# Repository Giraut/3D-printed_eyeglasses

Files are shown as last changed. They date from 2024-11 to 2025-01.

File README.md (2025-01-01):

# 3D-printed eyeglasses
### Version 1.4

Those are the CAD files for the frames of the spectacles I wear every day. When I break the frames, or if I want a new color for a bit of diversity, I simply print new frames and reuse the lenses.

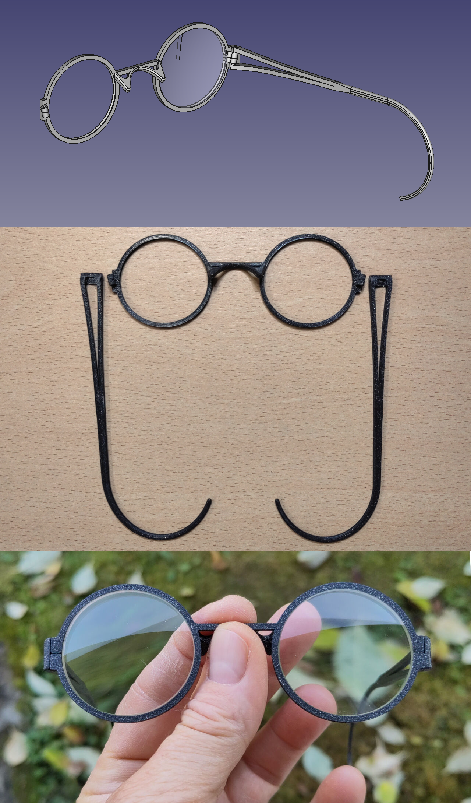
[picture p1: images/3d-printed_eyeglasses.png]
3D-printed eyeglasses

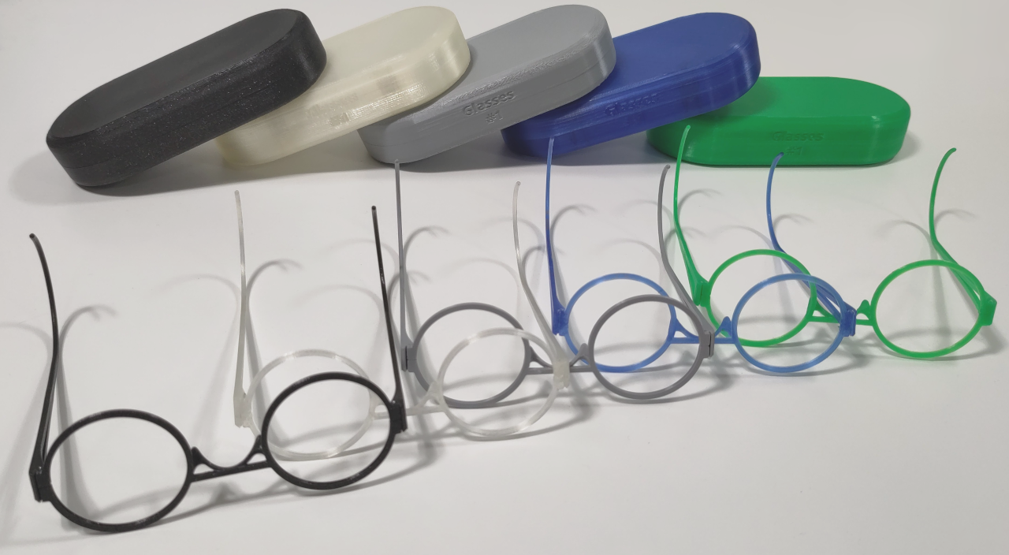
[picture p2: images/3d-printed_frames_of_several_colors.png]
3D-printed frames of several colors

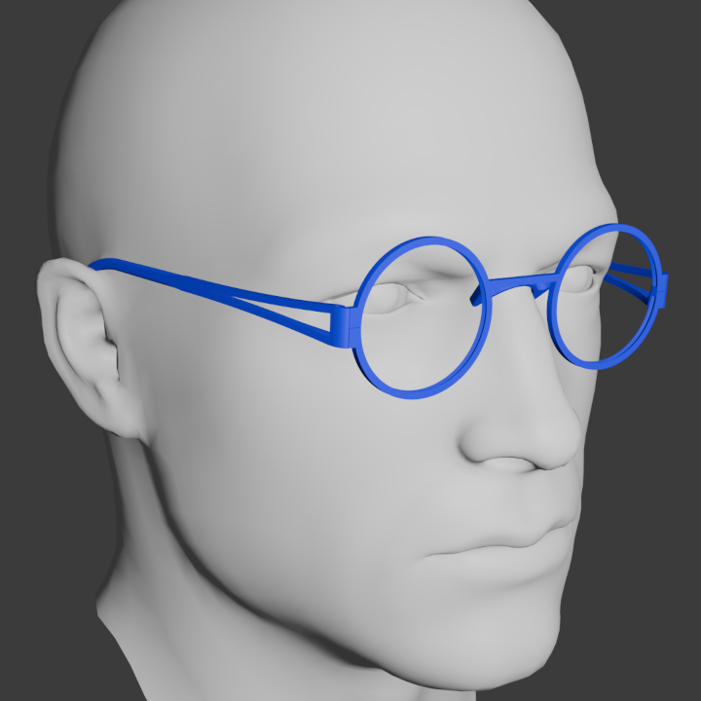
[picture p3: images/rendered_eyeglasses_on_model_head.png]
Rendered eyeglasses on model head


* [Files](#files)
* [Explanation of the registration tabs](#explanation-of-the-registration-tabs)
* [Printing](#printing)
* [Ordering lenses](#ordering-lenses)
* [Assembly](#assembly)
* [Customizing](#customizing)
* [Custom case](#custom-case)
* [Clip-on shades for round 38.8mm-diameter lenses](#clip-on-shades-for-round-388mm-diameter-lenses)
* [Clip-on shades with novelty mesh lenses](#clip-on-shades-with-novelty-mesh-lenses)
* [Custom case for the clip-on shades](#custom-case-for-the-clip-on-shades)

## Files

### Frames proper

Final frames in which the lenses are mounted. The lens holders feature lens registration tabs in the V-grooves at the split hinges (see below).

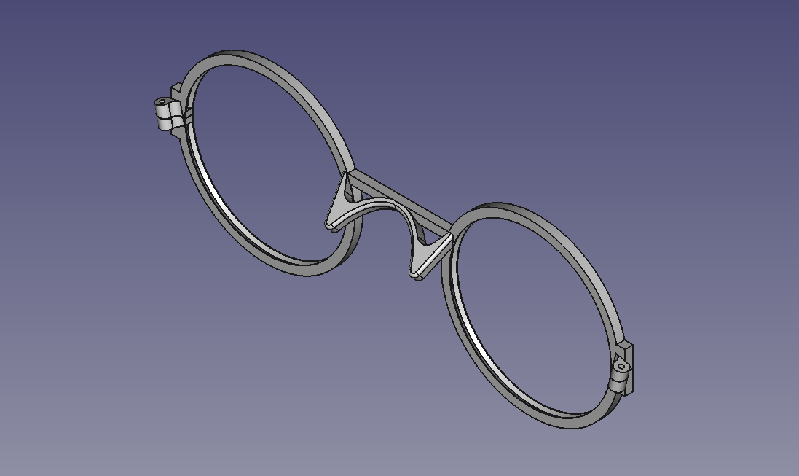
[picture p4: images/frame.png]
Frame


- [FreeCAD model for the frame](frame.FCStd)
- [3MF model for the frame](frame.3mf)

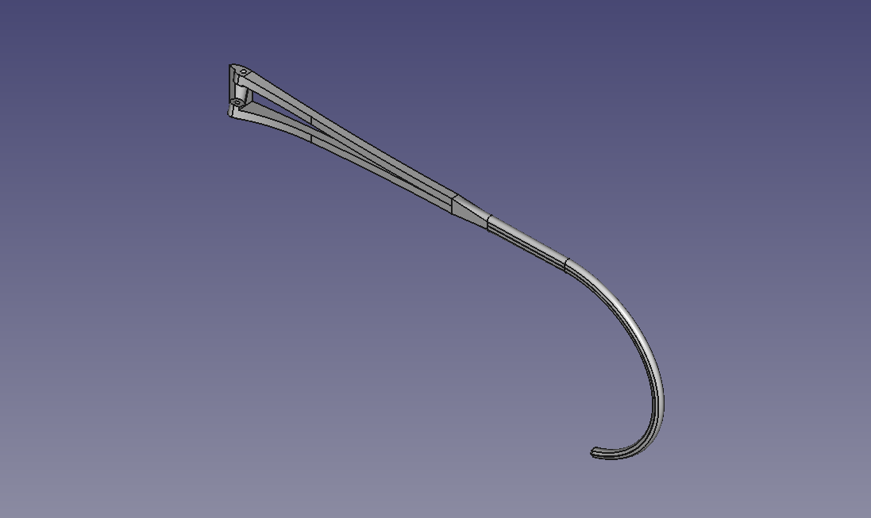
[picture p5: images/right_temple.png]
Right temple


- [FreeCAD model for the right temple](right_temple.FCStd) (the left temple is the mirror)
- [3MF model for the right temple](right_temple.3mf) (the left temple is the mirror)

### Template for the lens manufacturer

This template is supplied to the lens manufacturer: the lens holders have the same geometry as the final frames but the template is square and stiffer to facilitate mounting in the [lens edging machine](https://youtu.be/dKXUWH8gQLU), the V-groove is slightly deeper than the V-groove in the final frames and the registration tabs are absent to avoid snagging on the edging machine's tracer.

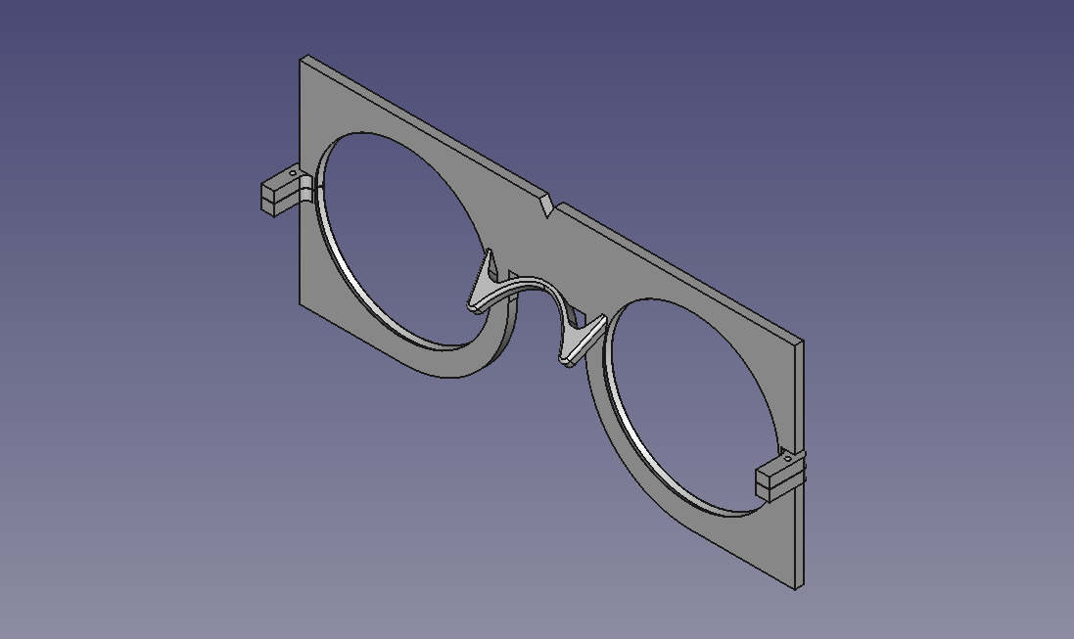
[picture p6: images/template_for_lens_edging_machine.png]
Template for lens edging machine


- [FreeCAD model for the edging machine template](template_for_lens_edging_machine.FCStd)
- [3MF model for the edding machine template](template_for_lens_edging_machine.3mf)

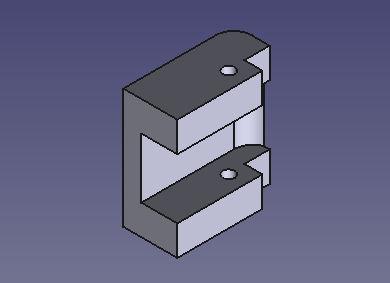
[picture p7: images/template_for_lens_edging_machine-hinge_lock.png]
Template for lens edging machine - Hinge lock


- [FreeCAD model for the edging machine template's fake hinges' locking piece](template_for_lens_edging_machine-hinge_lock.FCStd) (2 needed per template)
- [3MF model for the edging machine template's fake hinges' locking piece](template_for_lens_edging_machine-hinge_lock.3mf) (2 needed per template)

### Optional hinge pin jig

Optionally, this jig can be printed to hold the frames at a 13° angle so that the hinges' axes are vertical, to drive the pins in or out of the hinges with a press.

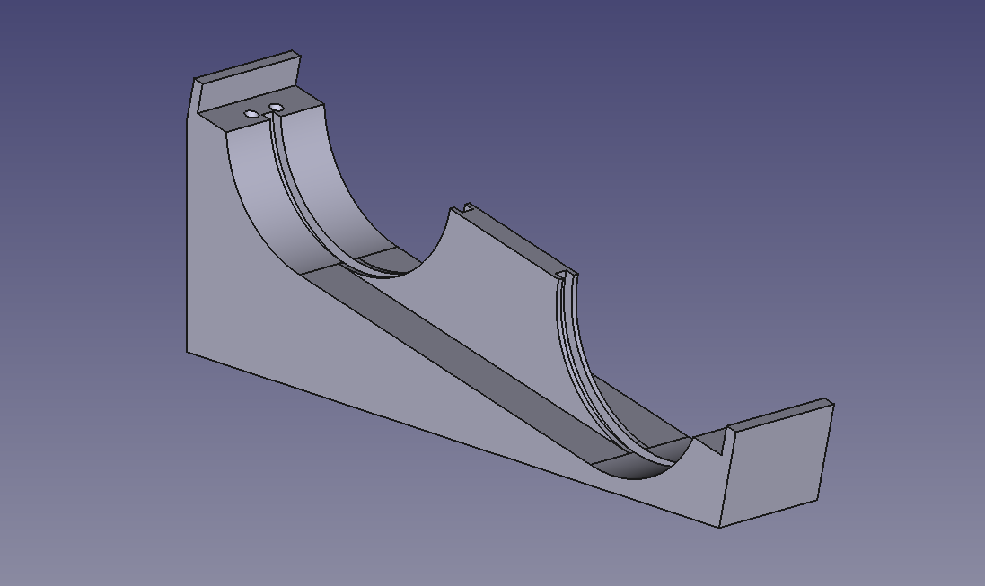
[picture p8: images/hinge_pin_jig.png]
Hinge pin jig


- [FreeCAD model for the hinge pin jig](hinge_pin_jig.FCStd)
- [3MF model for the hinge pin jig](hinge_pin_jig.3mf)

### Additional details for the lens manufacturer

A few details the lens manufacturer needs to choose the grinding wheel with the correct bevel profile ("hide-a-bevel"-type bevel, 120° angle) and the width and position of the lens registration tabs if you want them to file it for you - and they agree to do it of course:

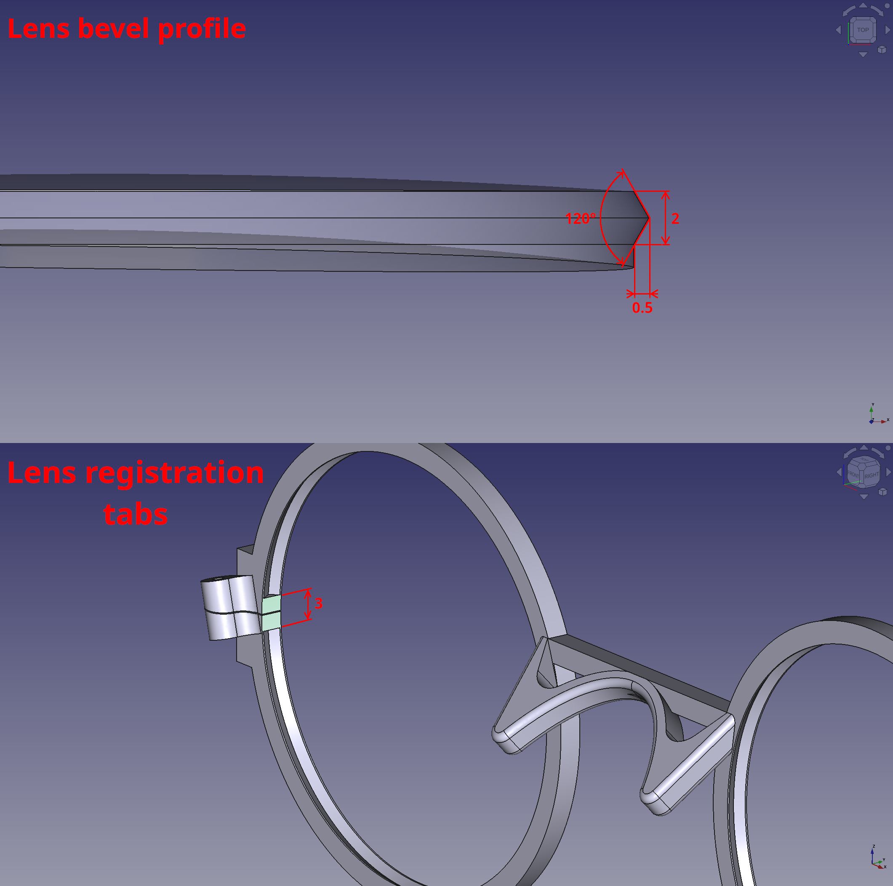
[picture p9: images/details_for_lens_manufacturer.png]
Details for the lens manufacturer


## Explanation of the registration tabs

The final frames feature lens registration tabs around the split hinges that interrupt the V-grooves. Those tabs orient the lenses correctly, which is important for astigmat lenses particularly. In this frame design, they also help lock the frame closed.

The tabs are required because the lenses are almost round. They provide a positive mechanical stop to prevent the lenses from shifting and turning in the lens holders, but they require filing a 3.5mm-wide notch in the lenses' bevel.

This type of lens registration is almost never used in round glasses because the frame itself is usually made of a material strong enough to clamp the lenses solidly in place, or the lenses are glued in place. Also, they're difficult to manufacture with traditional machining methods.

Those 3D-printed glasses provide very little clamping force, and glue isn't ideal to routinely and quickly install the lenses into new frames without damaging them. But it's trivially easy to print the registration tabs inside the V-grooves with a 3D printer.

Notching the bevel of the lenses is a one-off job, so this registration solution is more desirable if you want to change frames often. But it does require a square needle file, and more importantly, being handy with one. And it does require a small vise with rubber jaws, covering the lenses with scotch tape to avoid scratching them when they're clamped in the vise, and working up the nerves to files through your brand new, multi-hundred-dollar lenses if your prescription is very special.

If you don't think you can do it, point your lens manufacturer or your local optician to this page and ask them if they can do it for you. The lens manufacturer probably won't have time for this, but your local optician most certainly will if you order through them - but for a price of course. But again, it's a one-off job and after that, your new frames will always be free and you'll be able to mount the lenses yourself at home in a couple of minutes 🙂

## Printing

You can print the frames in any material you want, even PLA. Prefer low layer heights and print at lower speeds to get better details and more accuracy for the hinge pin holes and the V-groove profile. 0.2mm works, but 0.15mm or even 0.10mm is better. Print the lens holder front face down and the temples outer face down, so the visible surfaces when you wear the glasses look the smoothest and nicest.

## Ordering lenses

- Print the template and 2 fake hinge locking pieces.
- Split the hinges with an X-Acto knife or a razor blade.
- Close each hinge with a locking piece and secure it with a small piece of 1mm piano wire or similar.
- Send the template to the lens manufacturer or give it to your optician along with your prescription and tell them you want to receive the lenses mounted with the proper orientation in the lens holders with the 3 alignment dots marked on each lens! This is very important if you want to notch the bevels yourself. Otherwise ask the lens manufacturer or the optician to do it for you: they'll know what to do.

## Notching the lenses

- Insert the lenses in the template if they didn't come back from the lens manufacturer or the optician already mounted in it.
- Lightly squeeze the fake hinges with your fingers and line up all 6 alignment dots on the lenses.
- Close the fake hinges with the locking pieces.
- Ensure the lenses are positioned properly by placing the template on your nose like real glasses and ensuring you can see well through the lenses. Don't notch the lenses unless your vision is perfect at this point!
- With a thin sharpie, mark the location of the split hinge on each lens, front and back.
- Remove the lenses from the template and draw a line between the two marks on each lens, across the thickness of the lens, straddling the bevel.
- Cover the lenses in scotch tape to avoid damaging them in the vise.
- File a 3.5mm-wide notch into the bevel centered on the line on each lens. Don't file any deeper than the height of the bevel, otherwise the notch will be visible when the lens is mounted in the frame!

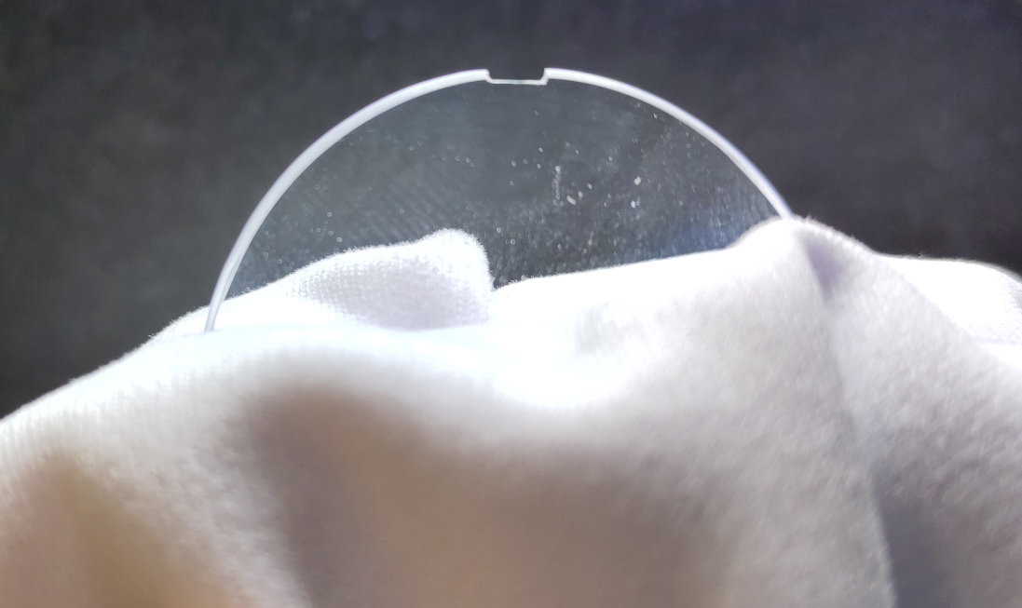
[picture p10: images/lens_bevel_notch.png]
Lens bevel notch


## Assembly

### Extra components needed

- 2 x [1x10mm dowel pins](https://www.mcmaster.com/91585A091/)

### Instructions

- After printing, crack off the supports.
- Ream the hinge pin holes on the frame and both temples with a 0.9mm drillbit, then as little as possible with a 1.0mm drillbit. Be careful when you insert the drillbits: the axes of the hinges are angled 13° vertically to allow the temples to fold up and fit in a regular glasses case. If you insert the drillbits straight vertically, you will damage the hinges!

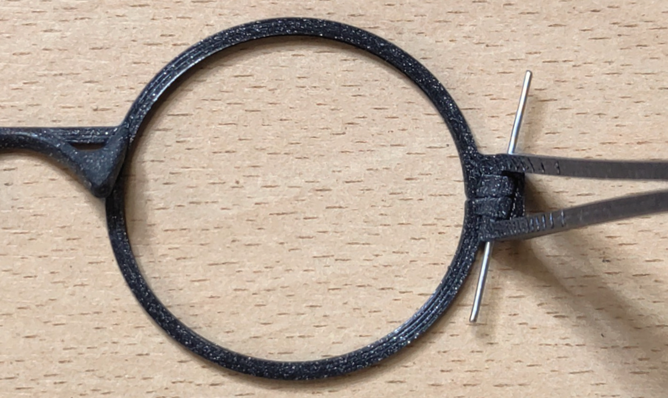
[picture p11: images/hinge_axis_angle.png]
Hinge axis angle

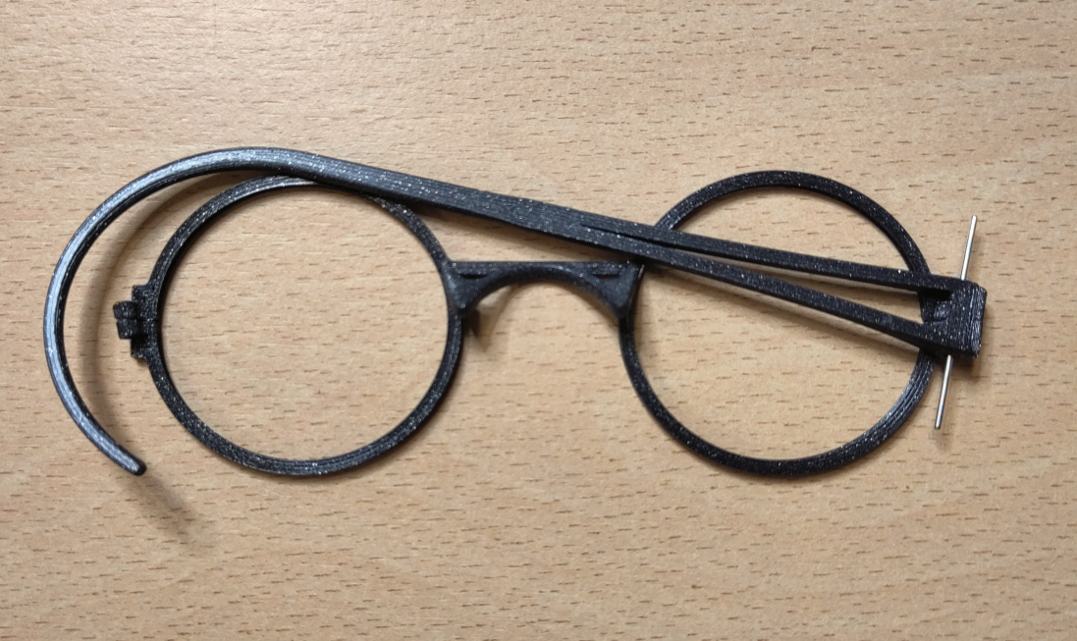
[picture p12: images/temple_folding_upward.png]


- Insert each lens into its holder with the notch facing the hinge.

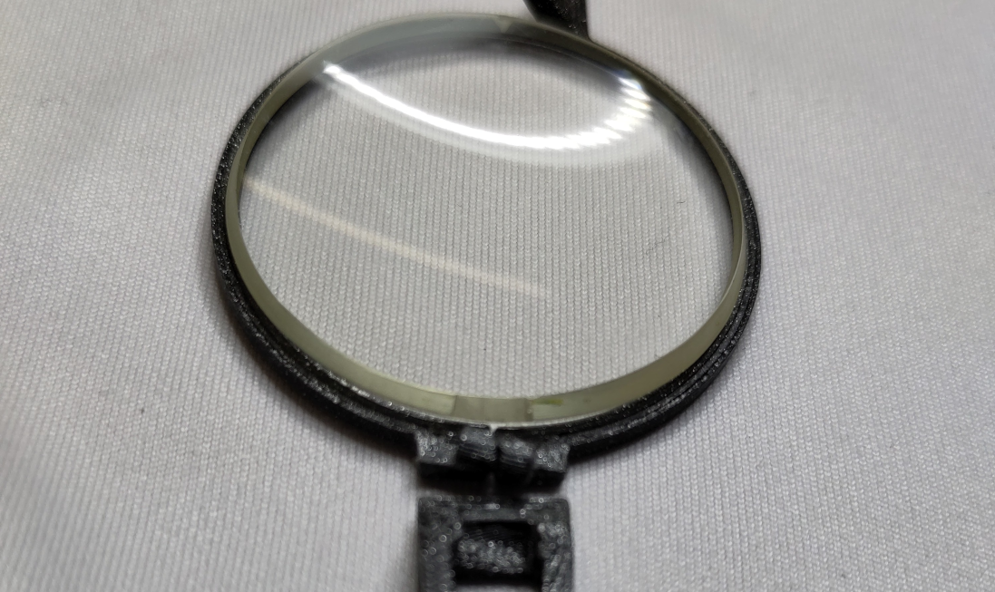
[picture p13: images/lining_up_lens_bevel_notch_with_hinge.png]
Lining up the lens bevel notch with the hinge


- Orient each lens until both halves of the hinge drop into the notch and the hinge closes completely.

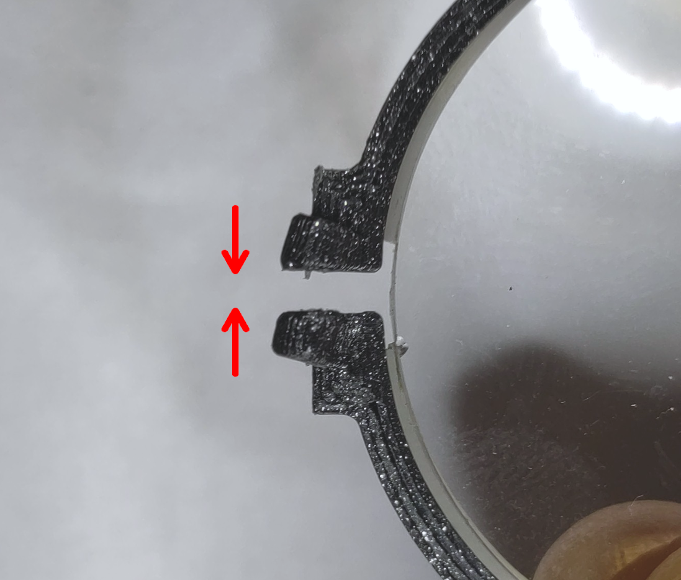
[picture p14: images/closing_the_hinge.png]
Closing the hinge


- Fit the temples onto the hinges.
- Drive a dowel pin through each temple and hinge to hold everything together.

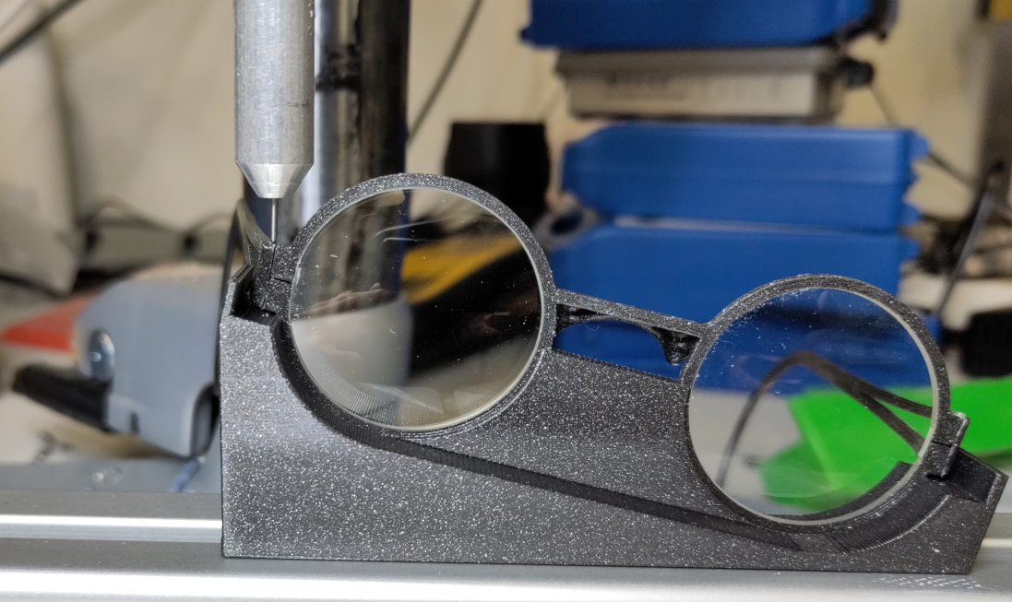
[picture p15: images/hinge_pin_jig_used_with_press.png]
Hinge pin jig used_with press


## Customizing

The parts in these FreeCAD model files are designed to create frames that fit me perfectly. But everybody's head is different.

The traditional way to adjust off-the-shelf eyeglasses is to soften and bend the frame and temples. But with 3D-printed frames, it is far better to print them exactly right for you: that way, little to no rework is required after printing new parts.

The frames should naturally drop on the roof of your nose, the temples should drop on the root of your ears and the temple wires should wrap around your ears such that:

- The glasses fit perfectly on your face with **ZERO** internal stress: PLA is quite bendy and these frames are very thin, so it doesn't take much tension to bend them out of shape and compromise the placement of the lenses. The frames should have the exact same shape on your face that they have when resting on a table.
- The glasses stay put on your nose and don't slide down.
- Each lens is perfectly centered on the corresponding eye.
- the lenses don't sit at an angle vertically - i.e. they're normal to your line of sight.

### Adjusting the temples splay

These frames are an older style design. They're copies of my nickel silver frames which I made myself some 20 years ago, themselves copies of vintage 1910 glasses I found at the flea market that I really liked. I believe this style is now called "John Lennon", but it's much older than that.

Frames in that style are much narrower than the wearer's head. The idea is to bring the lenses as close to the eyes as possible to provide a very wide field of view with small lenses and make the temples almost touch the sides of the head over their entire length (very convenient incidentally: you can sleep on your side with your glasses on without damaging them!).

For that reason, the frames are splayed to accommodate the width of your head. In other words, the temples are not parallel but opened up.

To adjust the splay, edit the `Hinge mid profile master sketch` in the temple's FreeCAD model and change the distance between the hinges and the root of your ear and the width of your head at that point:

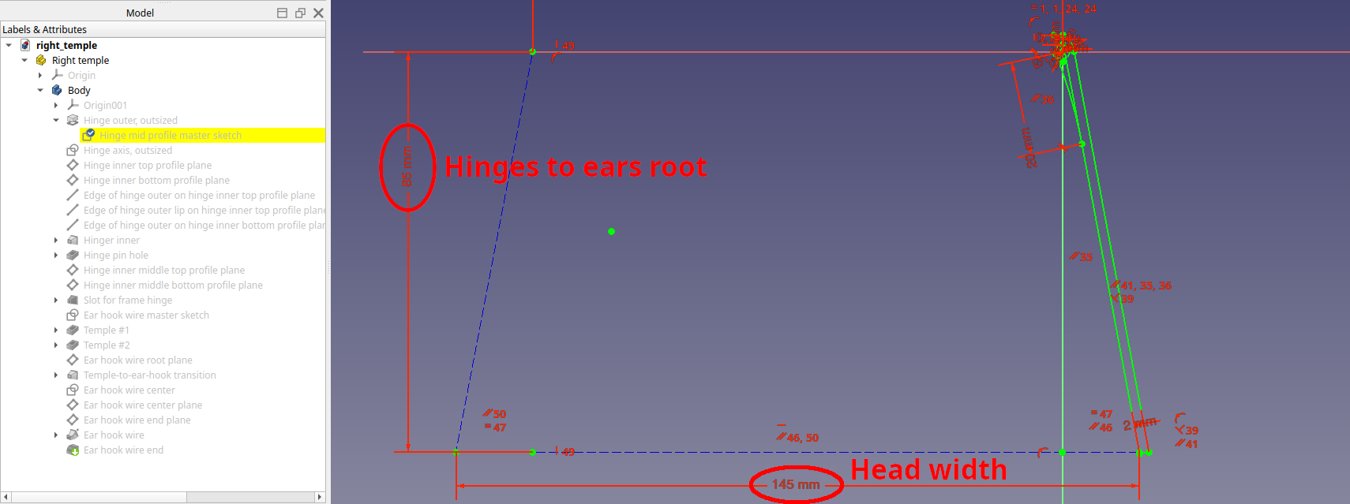
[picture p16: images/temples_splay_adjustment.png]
Temples splay adjustment


These dimensions aren't critical: they should get the splay angle in the ballpark. The temples should land on your ears without squeezing your head at all. But even if the opening is a few millimeters too narrow, the temple wires are flexible enough to bend a little without deforming the frame at the front.

Still, ideally the temples should only lightly graze the sides of your head.

## Adjusting the temple length, height and hook shape

Edit the `Ear hook wire master sketch` in the temple's FreeCAD model to change the length of the temples, modify the shape of the hooks if they don't wrap around your ears perfectly and adjust the temple drop (or rise if you reverse the dimension) to bring the lenses vertical:

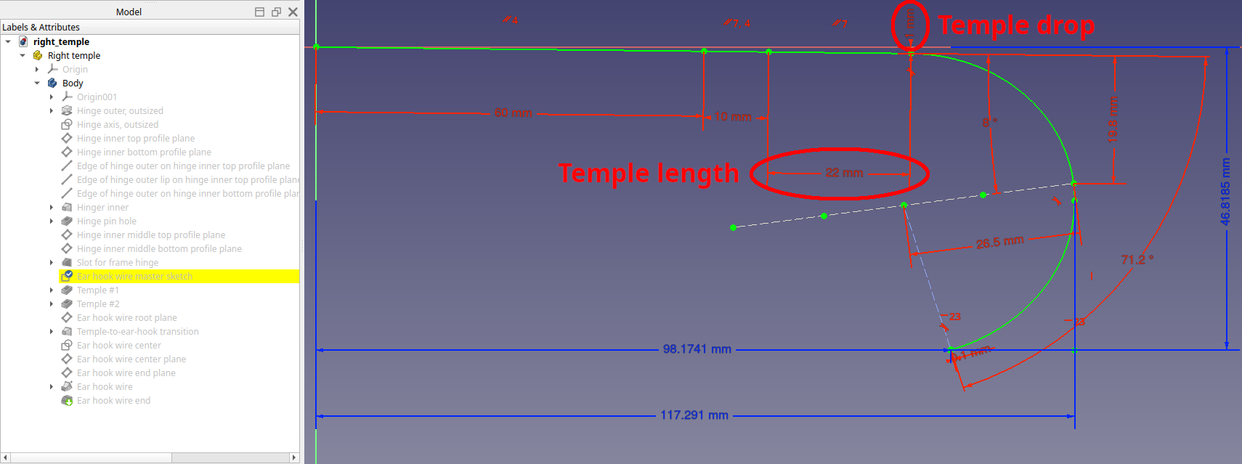
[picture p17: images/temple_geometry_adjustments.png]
Temple geometry adjustments


You may - and probably will - want adjust those parameters differently for the right and left temples if your eyes or your ears aren't level, or your ears have different shapes. Most people don't have perfectly symmetrical facial features, so it's perfectly normal.

To determine if the geometry of the left and right temple are correct:

- Don the glasses and let them sit on your nose and ears naturally.
- If a hook pulls on the back of your ear, the temple on that side is too short.
- If you pull gently on a temple and let go of it and that side of the frame stays low on your nose, the temple on that side is too long.
- If the end of a wire digs into the bottom of your ear, the wire hook on that side is too narrow.
- If the wire only rests on the top half of your ear and doesn't touch the bottom, the wire hook on that side is too wide.

Look straight ahead:

- If the frame looks like an unbroken circle and it looks like you're looking through a single hoop, the temple lengths and drops are dead-on.
- If the circle looks broken but the two halves look like they're the same diameters, you'll need to increase the drop on the side the half-circle appears lower.
- If the circle looks broken but the two halves look like they're at the same level but different diameters, you'll need to increase the length of the temple on the side the half-circle looks larger.

Those adjustments are sometimes mere millimeters and are done by trial and error - i.e. print, test for fit, re-print, re-test for fit... until the glasses fit perfectly and feel really comfortable.

It's a bit tedious but it's a one-off job: once it's done, you'll get perfectly-fitting glasses out of your printer each and every time.

## Adjusting the nose bridge

If the nose bridge is too narrow, it will feel like it's digging into the sides of your nose when wearing the glasses for a long time. If it's too wide, it will feel heavy on top of your nose over time.

You can adjust the shape of the bridge by editing the `Nose bridge profile` sketch in the frame's FreeCAD model. Unfortunately, this sketch has a lot of dependencies in other features of the model, and it's designed to merge perfectly with the decorative straight bridge at the front. So if you modify it too much, it will probably break the model. So some knowledge of modelling with FreeCAD is required to successfully alter the shape of the nose bridge so the model resolves correctly.

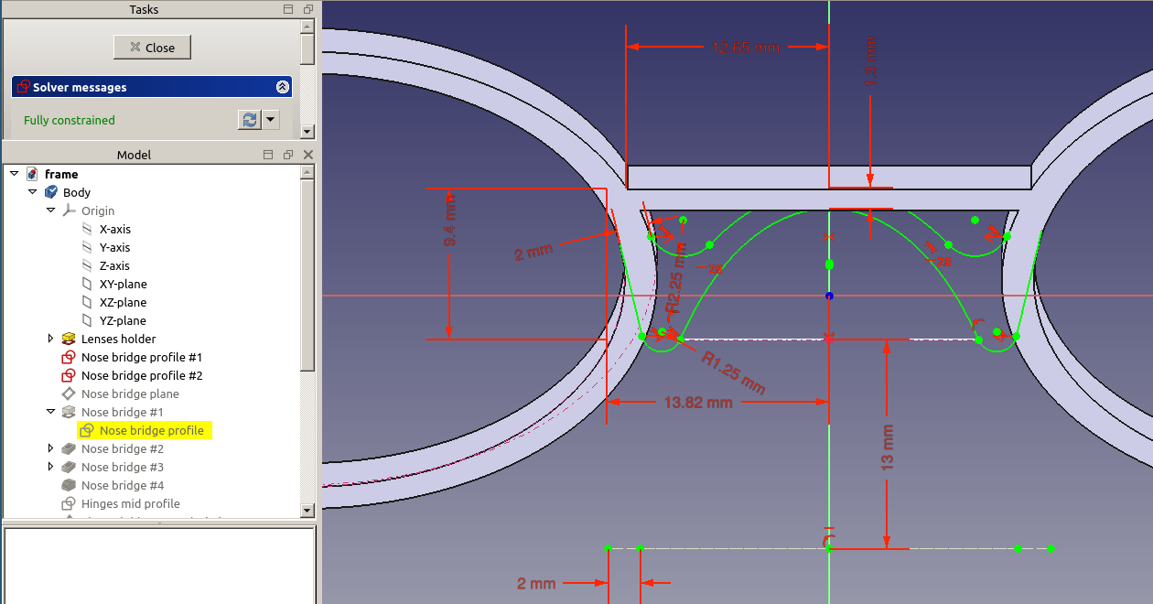
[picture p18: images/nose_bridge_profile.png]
Nose bridge profile


## Adjusting the lens holders' diameters

Depending on your particular printer and how the lens manufacturer edged the lenses exactly, the lenses may not fit perfectly inside the lens holders. You can modify the diameters of the lens holders by editing the `Lenses holder master sketch` in the frame's FreeCAD model:

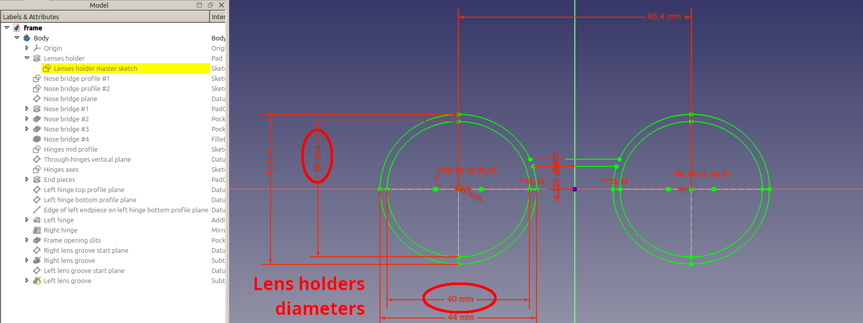
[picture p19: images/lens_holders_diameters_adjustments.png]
Lens holders diameters adjustments


The lens holders are elliptical and are nominally 40mm and 38mm in diameter. If the lenses fit loosely, reduce both diameters in steps of 0.1mm, reprint and retest for fit. If they fit too tight, increase both diameters similarly. Don't increase the diameters more tham 0.2mm to avoid compromising the frame's rigidity.

## Custom case

This case is custom-made for these glasses. It's designed to hold them by the edge of the frame only, without the lenses ever touching any part of the case, so the case doesn't need to be padded with soft material of any kind to prevent scratching:

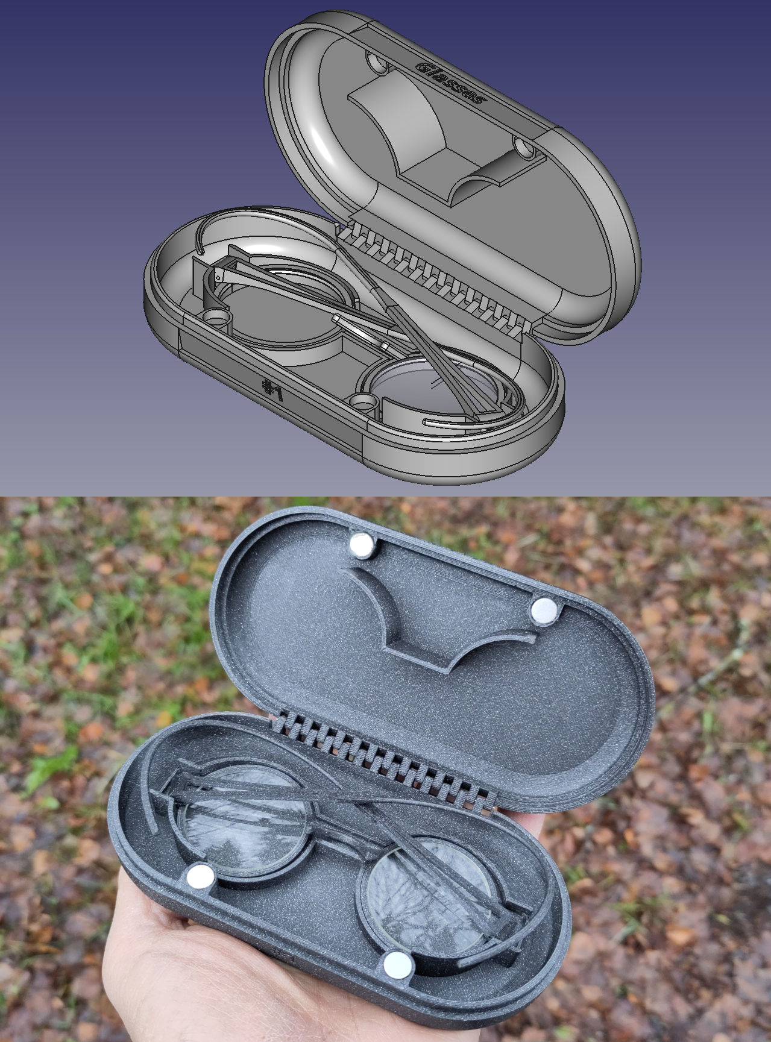
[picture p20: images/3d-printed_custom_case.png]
3D-printed custom case


The case is thick and very stiff, and the hinge is very solid. The case is held closed with 4 neodymium magnets. The lid is designed to pinch the edge of the frame when the case is closed, to lock the glasses in place and prevent them from shifting inside.

https://github.com/user-attachments/assets/2d8ead8f-aeec-490b-bac6-e63e706328ba

### Files

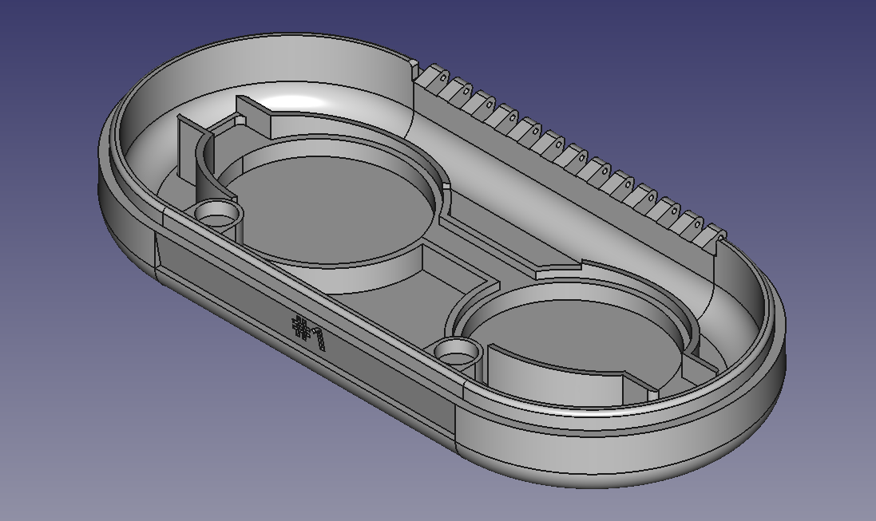
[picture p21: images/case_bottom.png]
Case bottom


- [FreeCAD model for the bottom of the case](case_bottom.FCStd)
- [3MF model for the bottom of the case](case_bottom.3mf)

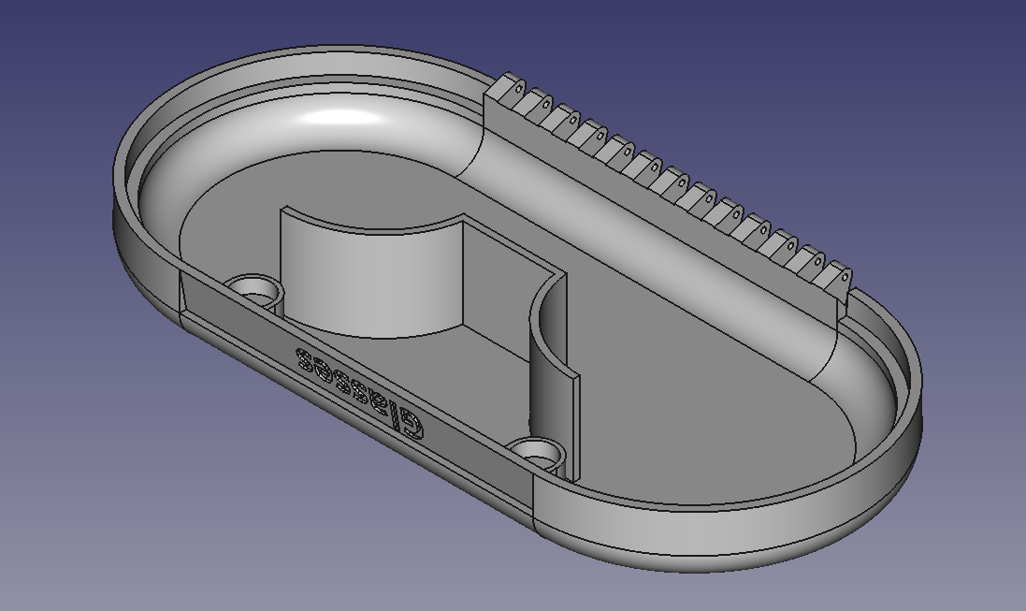
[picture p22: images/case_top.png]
Case top


- [FreeCAD model for the top of the case](case_top.FCStd)
- [3MF model for the top of the case](case_top.3mf)

### Assembly

#### Extra components needed

- 4 x [8x3mm neodymium magnet disks](https://uk.farnell.com/eclipse-magnetics/n825/neodymium-disc-magnet-8-x-3mm/dp/3376635)
- 79mm of [1mm piano wire](https://www.modelscenerysupplies.co.uk/piano-wire-1mm)

#### Instructions

- Epoxy 2 magnets in the magnet holders inside each half of the case. Pay attention to the orientation: opposing magnets should attract, not repel each other!
- Let the epoxy cure fully.
- Line up the top and bottom halves of the case.
- Slide the piano wire all the way through the hinge.

#### Customizing

The FreeCAD models for the bottom and top halves of the case include engraved-style lettering on the front edge. By default, the top half says "Glasses" and the bottom half says "#1". You can configure them to say whatever you want, like put your name on the case for example. To do so, edit the ShapeString in the model(s) you wish to change:

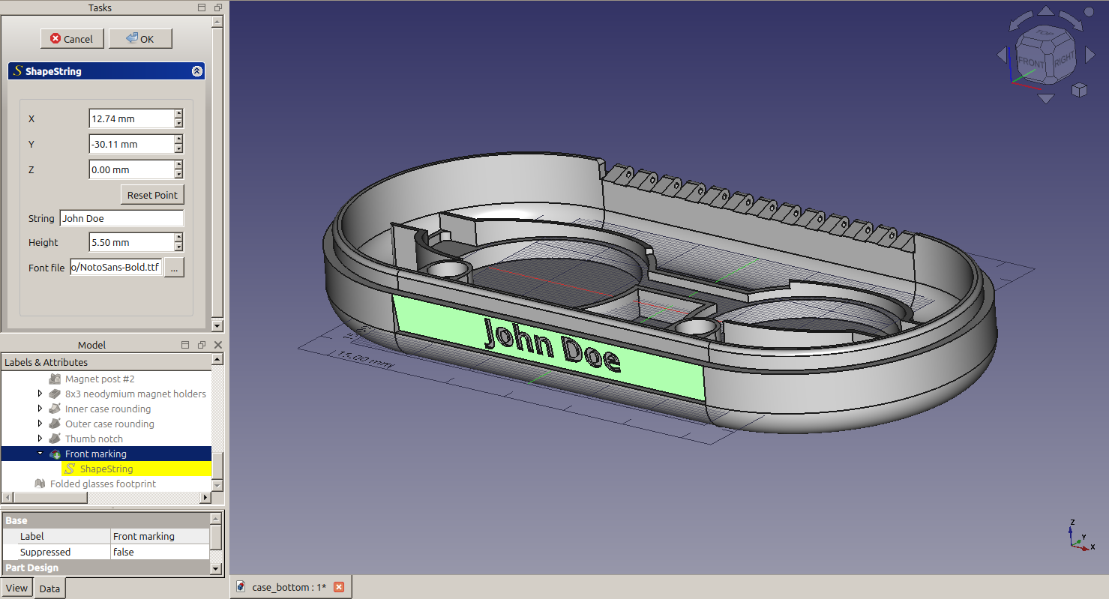
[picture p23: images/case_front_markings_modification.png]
Case front markings modifications


## Clip-on shades for round 38.8mm-diameter lenses

Attachment to turn your glasses into sunglasses.

These shades are designed to take round tinted lenses that are 38.8mm in diameter and 1.5mm thick. Specifically, they're designed for lenses harvested from cheap [Cailap Pouta sunglasses for children](https://cailap.com/fi/tuote/aurinkolasit/kids-aurinkolasit-pouta/).

I found several pairs of those half-price in an airport gift shop, so I bought all of them, kept the lenses and threw away the cheap plastic frames. If you find other suitable cheap donor sunglasses, modify the FreeCAD model accordingly.

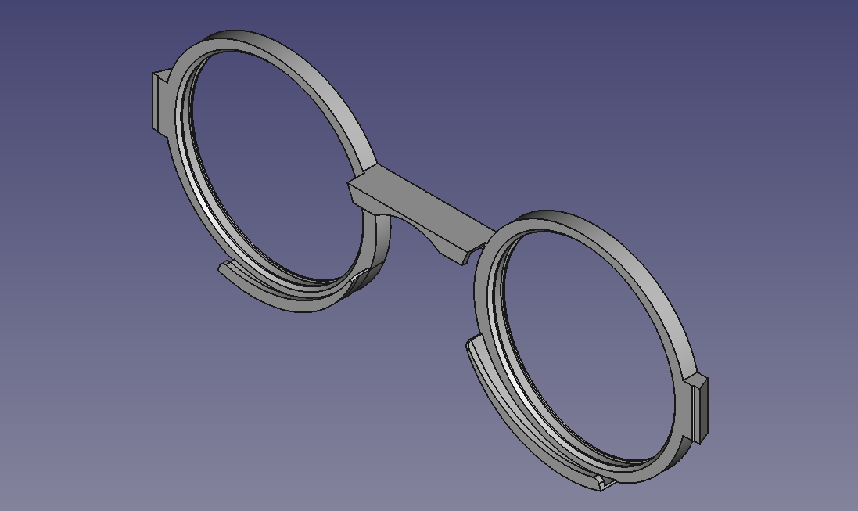
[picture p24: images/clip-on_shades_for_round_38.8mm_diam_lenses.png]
Clip-on shades for round 38.8mm-diameter lenses

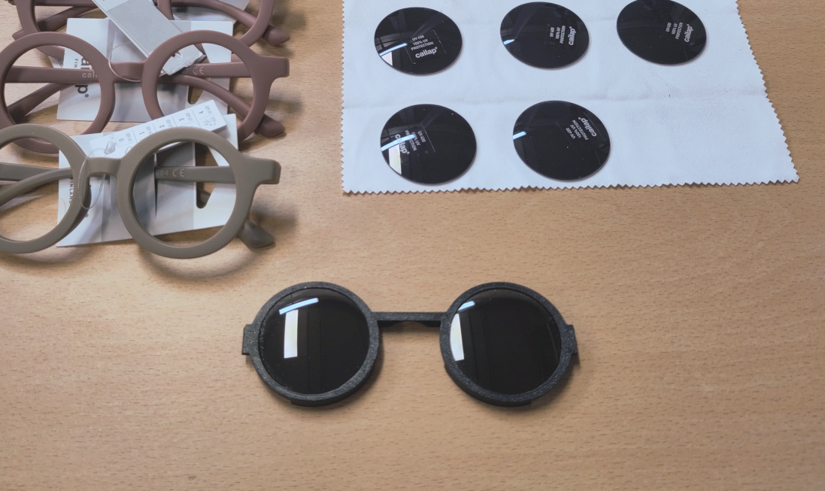
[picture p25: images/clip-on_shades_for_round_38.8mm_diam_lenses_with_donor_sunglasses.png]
Clip-on shades for round 38.8mm-diameter lenses


### Files

- [FreeCAD model for the clip-on shades for round 38.8mm-diameter lenses](clip-on_shades_for_round_38.8mm_diam_lenses.FCStd)
- [3MF model for the clip-on shades for round 38.8mm-diameter lenses](clip-on_shades_for_round_38.8mm_diam_lenses.3mf)

## Clip-on shades with novelty mesh lenses

Attachment to turn your glasses into sunglasses of sorts. The "lenses" are in fact very fine 3D-printed mesh, so vision through them is not perfect. But it's plenty good enough to do sports for example. Their main advantage is that they don't require real lenses and they're almost free.

*Note: these shades aren't eye-safe. They'll let UV light through. If your regular, clear lenses don't have a UV coating, please glue a layer of UV-filtering material on the inside!*

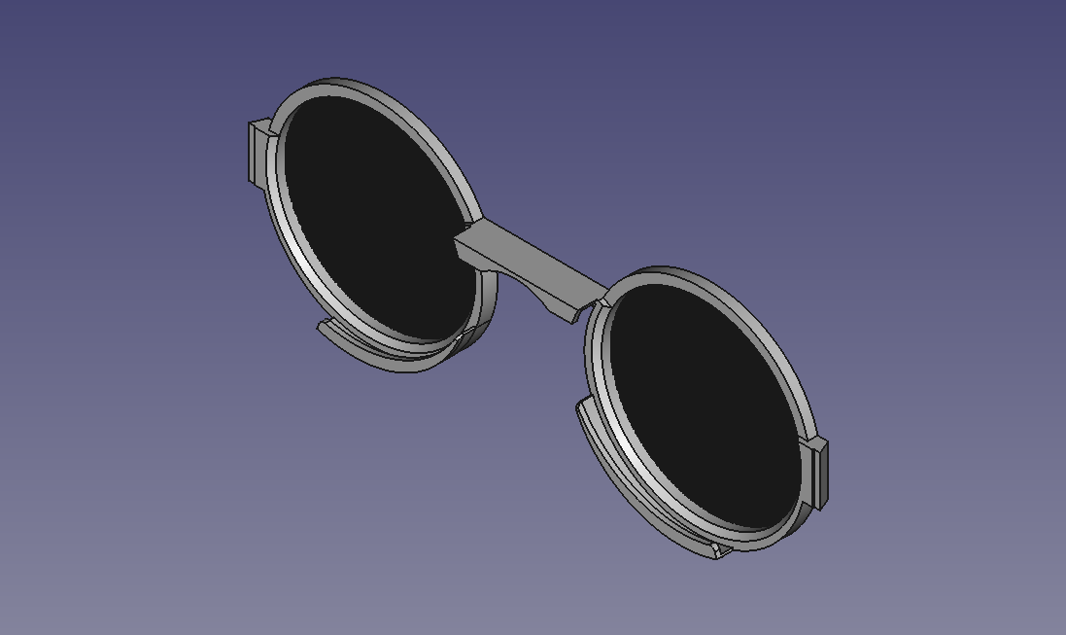
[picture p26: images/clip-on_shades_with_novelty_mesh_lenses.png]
Clip-on shades with novelty mesh lenses

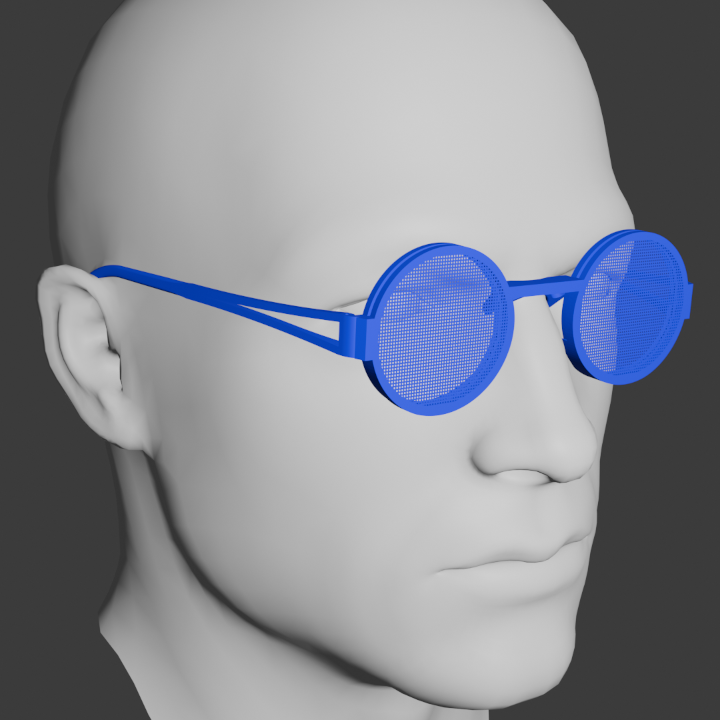
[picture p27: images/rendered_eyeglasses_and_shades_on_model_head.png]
Rendered eyeglasses and shades on model head


### Files

- [FreeCAD model for the clip-on shades with novelty mesh lenses](clip-on_shades_with_novelty_mesh_lenses.FCStd)
- [3MF model for the clip-on shades with novelty mesh lenses](clip-on_shades_with_novelty_mesh_lenses.3mf)

The clip-on shades with novelty mesh lenses are designed to be printed with a 0.4mm nozzle at a 0.1mm layer height, including the first layer.

## Custom case for the clip-on shades

This case is custom-made for the clip-on shades. Like the eyeglasses case, it's designed to hold them by the edge of the frame only, without the lenses ever touching any part of the case, so the case doesn't need to be padded with soft material of any kind to prevent scratching:

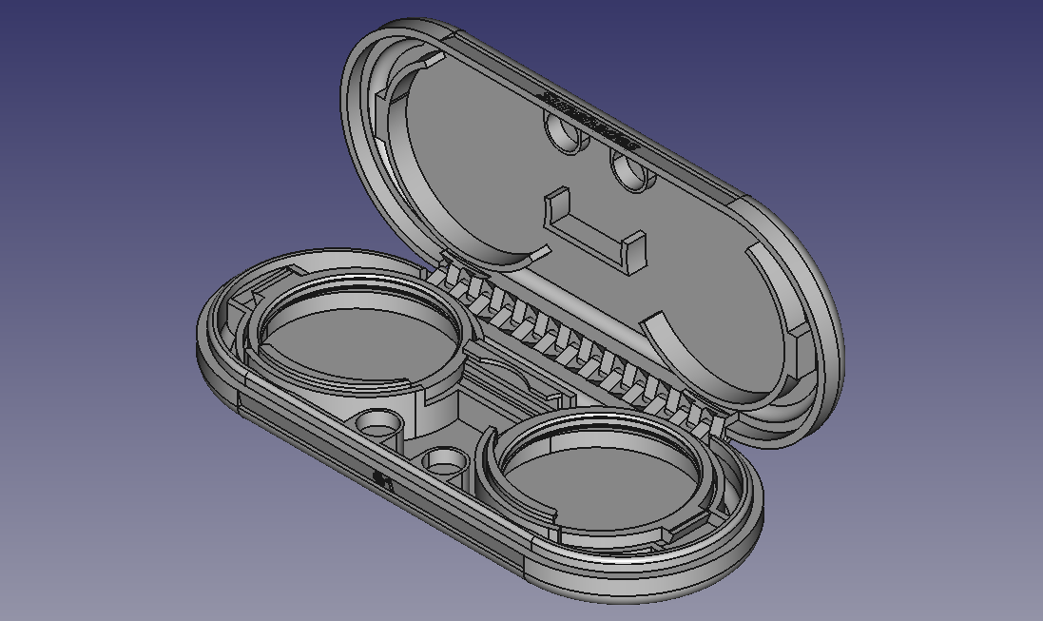
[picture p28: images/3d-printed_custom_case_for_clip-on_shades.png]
3D-printed custom case for the clip-on shades


The case is thick and very stiff, and the hinge is very solid. The case is held closed with 4 neodymium magnets. The lid is designed to pinch the edge of the frame when the case is closed, to lock the clip-on shades in place and prevent them from shifting inside.

https://github.com/user-attachments/assets/a3490ee9-8b56-42ed-8718-a661a9f8ea53

### Files

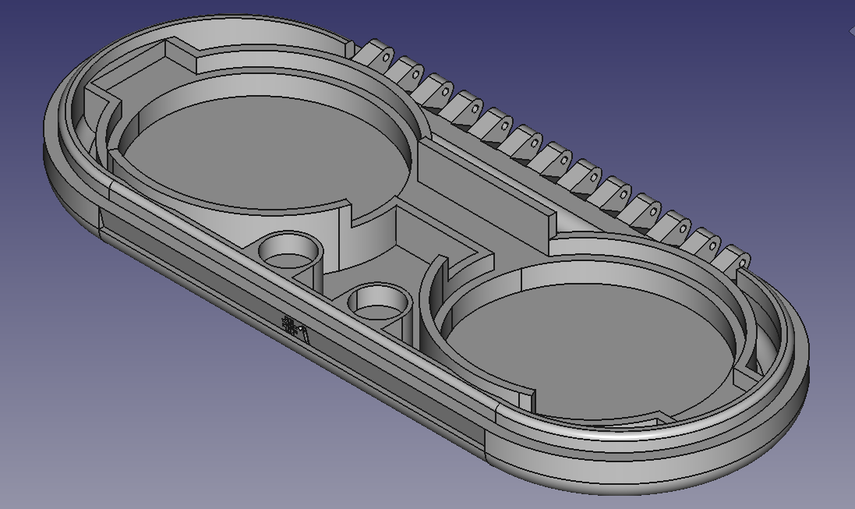
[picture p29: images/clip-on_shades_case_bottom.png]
Clip-on shades case bottom


- [FreeCAD model for the bottom of the clip-on shades case](clip-on_shades_case_bottom.FCStd)
- [3MF model for the bottom of the clip-on_shades_case](clip-on_shades_case_bottom.3mf)

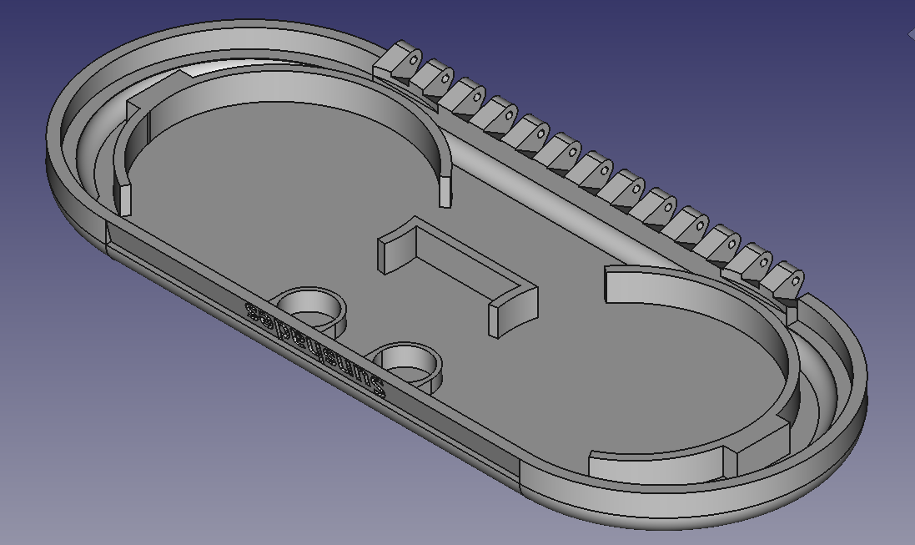
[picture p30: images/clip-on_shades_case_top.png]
clip-on_shades_case top


- [FreeCAD model for the top of the clip-on shades case](clip-on_shades_case_top.FCStd)
- [3MF model for the top of the clip-on shades case](clip-on_shades_case_top.3mf)

### Assembly

#### Extra components needed

- 4 x [8x3mm neodymium magnet disks](https://uk.farnell.com/eclipse-magnetics/n825/neodymium-disc-magnet-8-x-3mm/dp/3376635)
- 78mm of [1mm piano wire](https://www.modelscenerysupplies.co.uk/piano-wire-1mm)

#### Instructions

- Epoxy 2 magnets in the magnet holders inside each half of the case. Pay attention to the orientation: opposing magnets should attract, not repel each other!
- Let the epoxy cure fully.
- Line up the top and bottom halves of the case.
- Slide the piano wire all the way through the hinge.

#### Customizing

The FreeCAD models for the bottom and top halves of the clip-on shades case include engraved-style lettering on the front edge. By default, the top half says "Sunshades" and the bottom half says "#1". Like the eyeglasses case, you can configure them to say whatever you want by editing the ShapeString in the model(s) you wish to change.

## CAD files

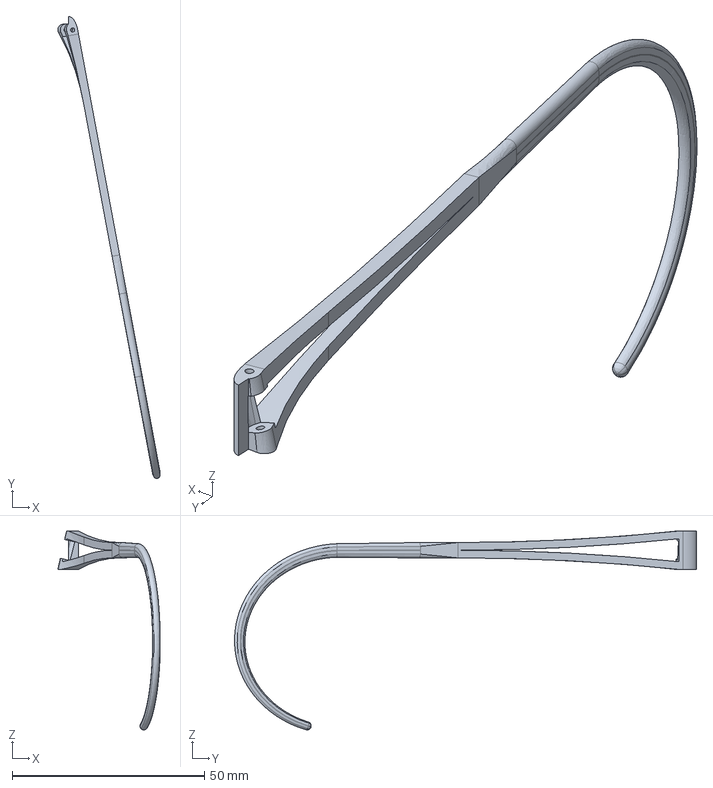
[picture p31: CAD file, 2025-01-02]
right_temple.FCStd
26.7 x 120.2 x 51.8 mm

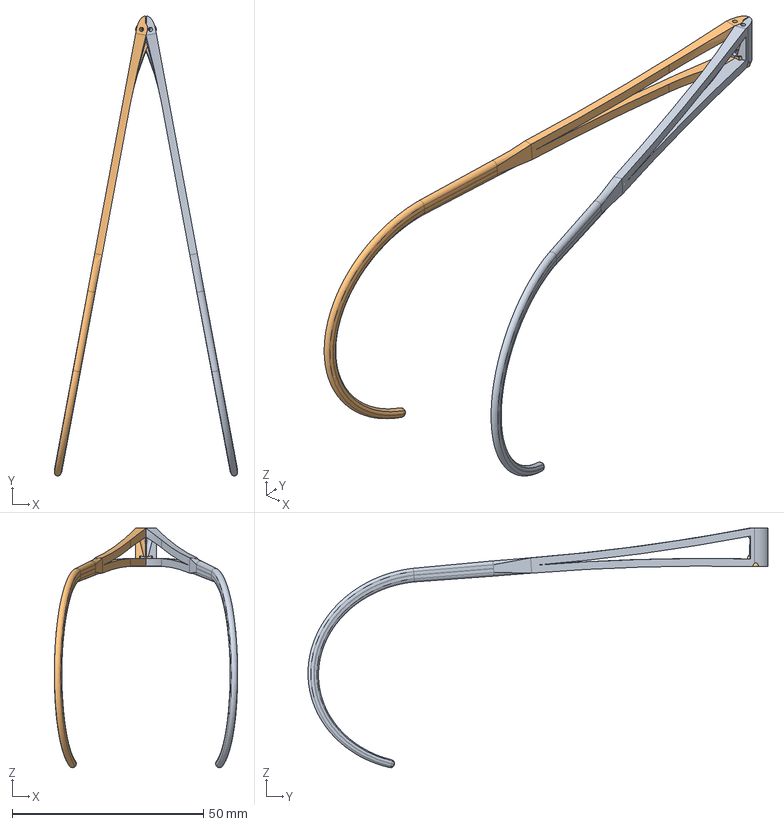
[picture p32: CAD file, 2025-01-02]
left_temple.FCStd
47.9 x 120.1 x 62.5 mm
Left temple

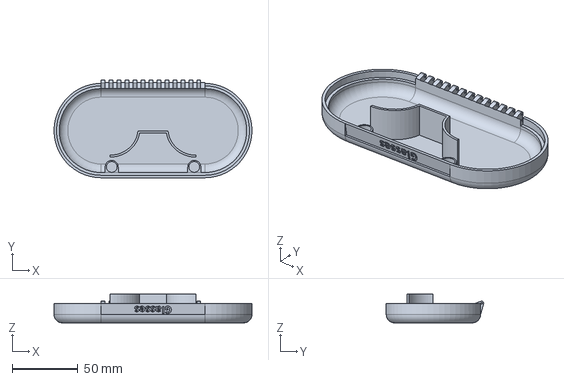
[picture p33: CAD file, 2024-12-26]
case_top.FCStd
151.0 x 74.4 x 22.0 mm

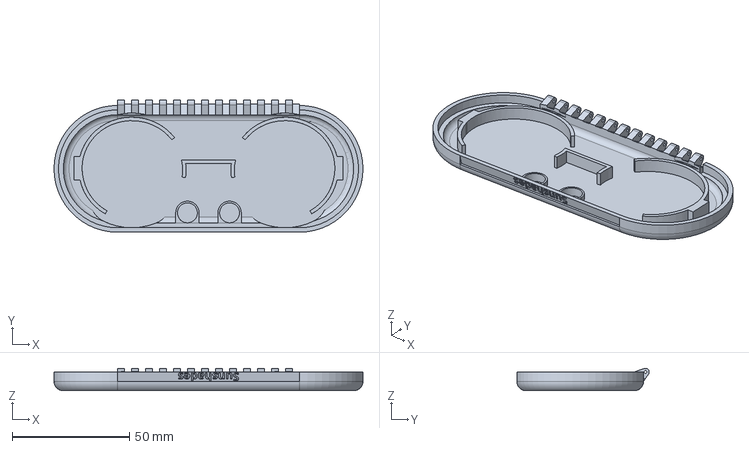
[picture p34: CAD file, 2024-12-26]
clip-on_shades_case_top.FCStd
131.9 x 56.5 x 9.60 mm

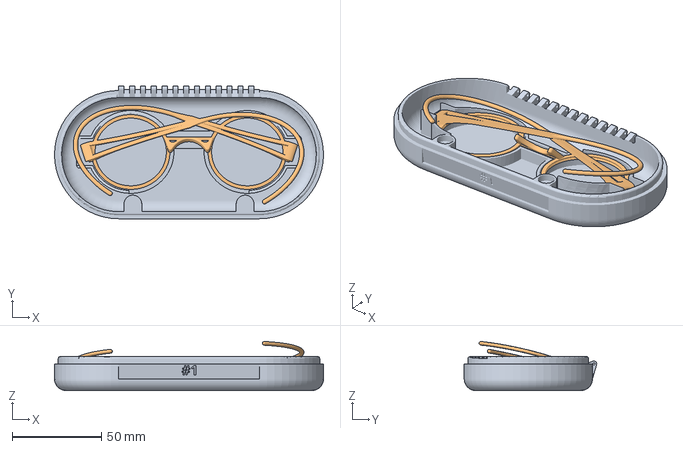
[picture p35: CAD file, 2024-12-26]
case_bottom.FCStd
151.0 x 74.4 x 27.6 mm
Folded glasses footprint

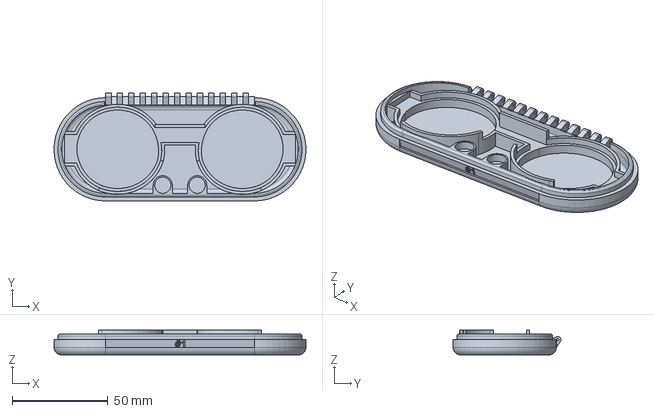
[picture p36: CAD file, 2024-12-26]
clip-on_shades_case_bottom.FCStd
131.9 x 56.5 x 13.0 mm

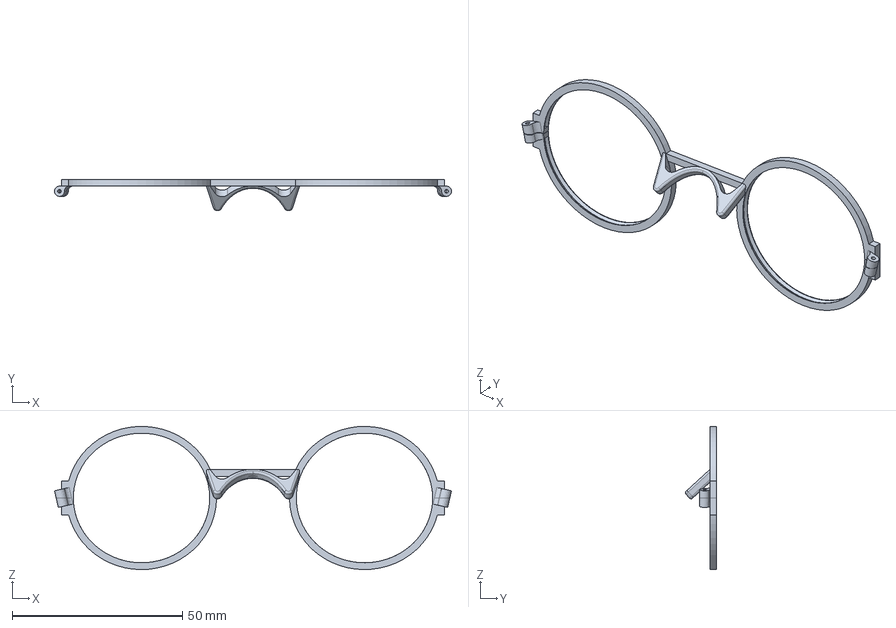
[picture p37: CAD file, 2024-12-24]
frame.FCStd
116.4 x 9.20 x 42.0 mm

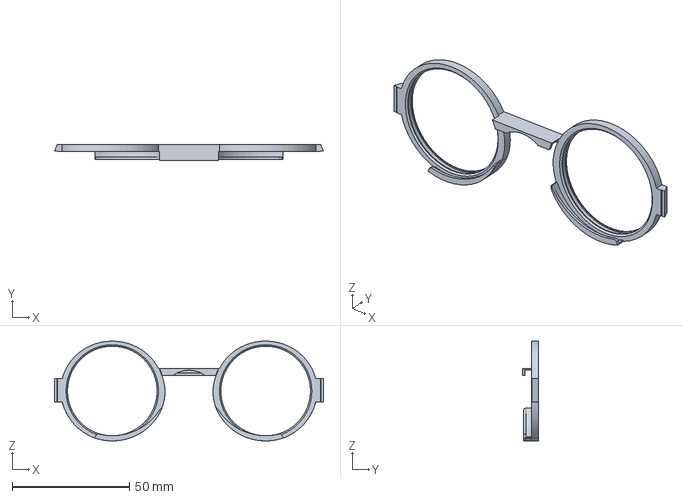
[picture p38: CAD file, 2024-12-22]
clip-on_shades_for_round_38.8mm_diam_lenses.FCStd
114.7 x 6.70 x 42.6 mm

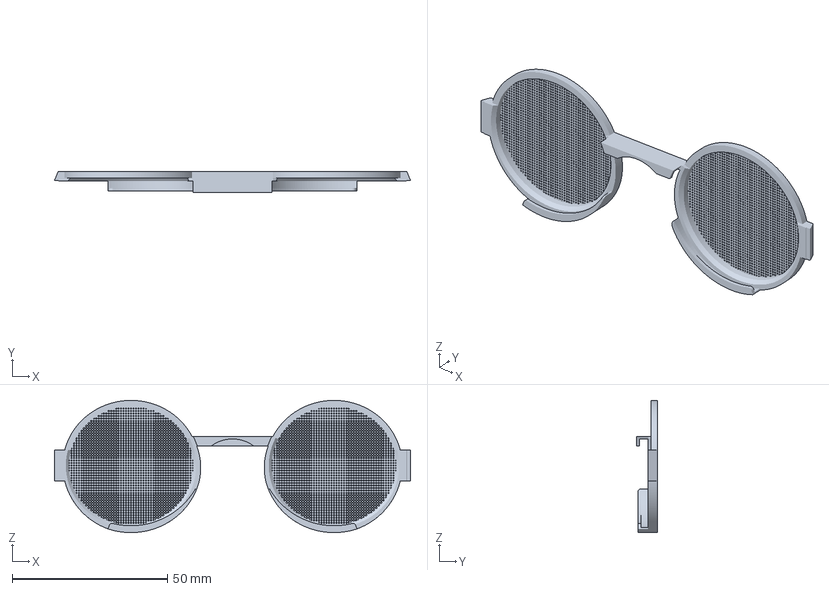
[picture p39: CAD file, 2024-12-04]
clip-on_shades_with_novelty_mesh_lenses.3mf
114.7 x 6.70 x 42.6 mm

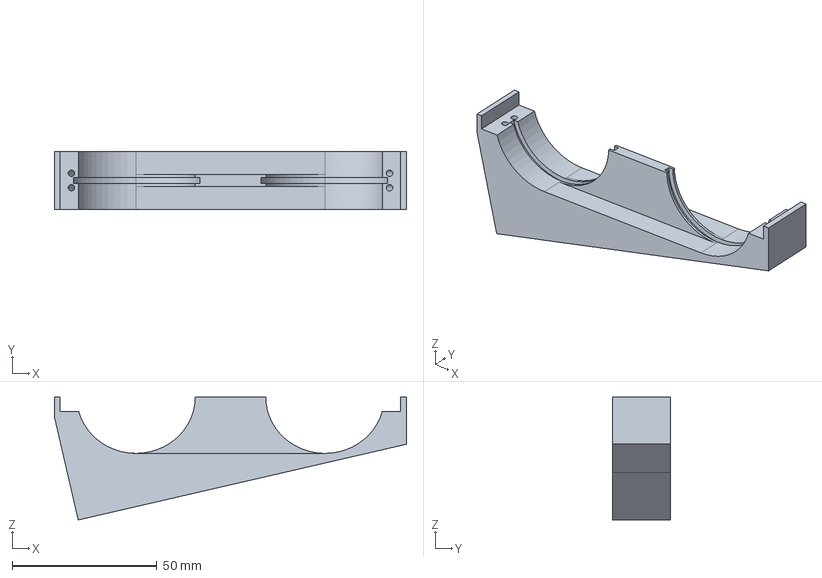
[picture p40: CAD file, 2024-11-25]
hinge_pin_jig.FCStd
121.8 x 20.0 x 42.6 mm

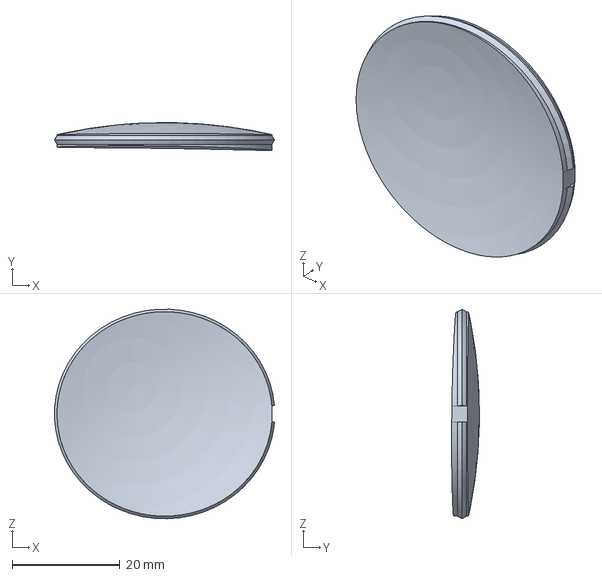
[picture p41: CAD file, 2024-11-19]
lens_example.FCStd
40.9 x 5.18 x 39.0 mm

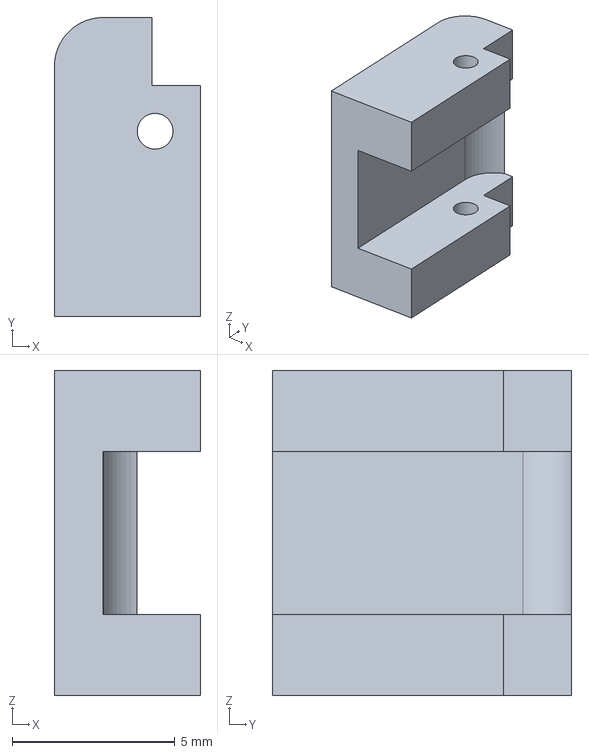
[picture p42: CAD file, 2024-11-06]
template_for_lens_edging_machine-hinge_lock.FCStd
4.50 x 9.20 x 10.0 mm

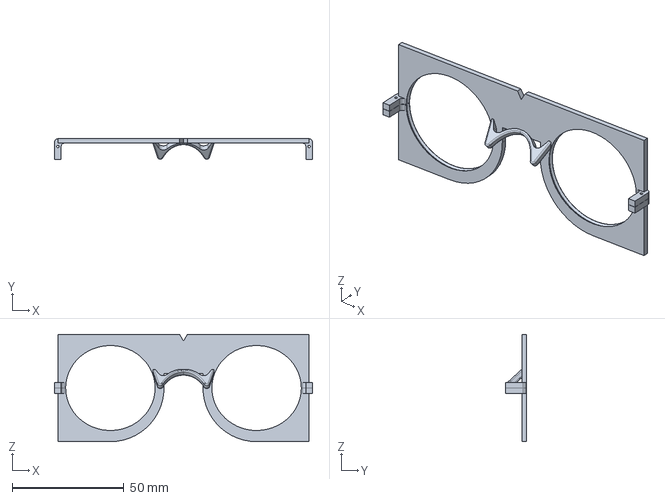
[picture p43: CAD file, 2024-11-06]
template_for_lens_edging_machine.FCStd
115.4 x 9.20 x 48.0 mm

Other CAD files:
case_assembly.FCStd
clip-on_shades_case_assembly.FCStd
folded_glasses_assembly.FCStd
case_bottom.3mf
case_top.3mf
clip-on_shades_case_bottom.3mf
clip-on_shades_case_top.3mf
clip-on_shades_for_round_38.8mm_diam_lenses.3mf
frame.3mf
hinge_pin_jig.3mf
left_temple.3mf
lens_example.3mf
right_temple.3mf
template_for_lens_edging_machine-hinge_lock.3mf
template_for_lens_edging_machine.3mf

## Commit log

2024-11-06 Stiffer template frame and added centerline mark
    [template_for_lens_edging_machine.3mf, template_for_lens_edging_machine.FCStd]
2024-11-06 Removed stray edge
    [template_for_lens_edging_machine-hinge_lock.3mf, template_for_lens_edging_machine-hinge_lock.FCStd]
2024-11-06 Pin hole diam. 1.0mm > 1.1mm
    [template_for_lens_edging_machine-hinge_lock.3mf, template_for_lens_edging_machine-hinge_lock.FCStd, template_for_lens_edging_machine.3mf, template_for_lens_edg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]
2024-11-06 Angled the hinge axes 15 degrees vertically so the temples fold upward and the folded spectacles fit inside a regular glasses case
    [frame.3mf, frame.FCStd, right_temple.3mf, right_temple.FCStd]
2024-11-06 Updated the documentation to mention the angled hinge axes. Added more images and explanations.
2024-11-06 Updated the image with details for lens manufacturers to show the new hinge design
2024-11-07 Added photo of frames printed with different color filaments
2024-11-07 Added model of the hinge pin jig, images and instructions
    [hinge_pin_jig.3mf, hinge_pin_jig.FCStd]
2024-11-08 Added splay to the temples so they don't need rework to open up farther than 90 degrees and lengthened the wires by 4mm
    [right_temple.3mf, right_temple.FCStd]
2024-11-08 Added left temple with different drop setting for reference
    [left_temple.3mf, left_temple.FCStd]
2024-11-09 Renamed the main nose bridge profile sketch
    [frame.FCStd]
2024-11-09 Added instructions to customize the frames for fit
2024-11-12 Added custom case
    [case_bottom.3mf, case_bottom.FCStd, case_top.3mf, case_top.FCStd]
2024-11-13 Corrected the FreeCAD models so they assemble correctly in the assembly workbench
    [case_bottom.3mf, case_bottom.FCStd, case_top.3mf, case_top.FCStd]
2024-11-15 Made the model recompute without error with larger temple drops and lengths
    [right_temple.3mf, right_temple.FCStd]
2024-11-15 Adjusted for more comfortable fit
    [left_temple.3mf, left_temple.FCStd]
2024-11-17 Removed the marked transition between the hinge and the wire in the temple profile so it looks better and so the root of the wire is stronger
    [left_temple.3mf, left_temple.FCStd, right_temple.3mf, right_temple.FCStd]
2024-11-18 Redrew the lens bevel profile for clarity
2024-11-18 Corrected undefined references in models
    [case_bottom.FCStd, case_top.FCStd, frame.FCStd]
2024-11-18 Fixed left temple's aspect
    [left_temple.FCStd]
2024-11-18 Added example of a lens with a notched bevel
    [lens_example.FCStd]
2024-11-18 Added assemblies for the folded glasses, and for the case containing the glasses
    [case_assembly.FCStd, folded_glasses_assembly.FCStd]
2024-11-19 Increased lens curvature to emphasize the bevel
    [lens_example.FCStd]
2024-11-20 Added 3MF file for the lens example
    [lens_example.3mf]
2024-11-21 Corrected the hinges' loft
    [frame.3mf, frame.FCStd]
2024-11-21 Corrected frame hinges in illustrations
2024-11-25 Redesigned the temples to be straight all the way to the root of the ears. Redesigned the wire hooks to hug the curvature of the back of the ears better. Changed the hinge tilt from 15 degrees to 13 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
    [folded_glasses_assembly.FCStd, frame.3mf, frame.FCStd, hinge_pin_jig.3mf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]
2024-11-25 Lenghtened the temple slightly. Made the wire end a bit shorter to aid donning the glasses.
    [left_temple.FCStd]
2024-11-25 Made the wire end a bit shorter to aid donning the glasses
    [right_temple.FCStd]
2024-12-04 Added model and images for the clip-on shades
    [clip-on_shades.3mf]
2024-12-19 Added model for clip-on shades designed to mount round 38.8mm-diameter lenses
    [clip-on_shades_for_round_38.8mm_diam_lenses.3mf, clip-on_shades_for_round_38.8mm_diam_lenses.FCStd, clip-on_shades_with_novelty_mesh_lenses.3mf]
2024-12-22 Added custom case for the clip-on shades
    [clip-on_shades_case_assembly.FCStd, clip-on_shades_case_bottom.3mf, clip-on_shades_case_bottom.FCStd, clip-on_shades_case_top.3mf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]
2024-12-22 Increased the clearance for the bottom edge of the bottom frame holder, to prevent it catching on the lip of the real, somewhat flexible case upon closing
    [clip-on_shades_case_top.3mf, clip-on_shades_case_top.FCStd]
2024-12-22 Added missing anchor link to the custom clip-on shades case
    [clip-on_shades_case_bottom.3mf]
2024-12-24 Corrected the frame's FreeCAD model for easier adjustment of the lens holders' diameters. Added instructions to adjust the fit of the lenses.
    [frame.FCStd]
2024-12-24 Small correction of the hinge geometry of the bottom half of the case
    [case_bottom.3mf, case_bottom.FCStd]
2024-12-26 Added thumb notches to make opening the case easier
    [case_assembly.FCStd, case_bottom.3mf, case_bottom.FCStd, case_top.3mf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]
2024-12-26 Sharper lens bevel notch photo
2024-12-26 Corrected 3mf for the case's bottom that erroneously contained the top as well
    [case_bottom.3mf, clip-on_shades_case_bottom.3mf]
2024-12-27 Corrected the width of the lens bevel notches
2024-12-28 Added demo video for the clip-on shades case and replaced the demo video for the eyeglasses case
2025-01-02 Lengthened the tips of the temples 3mm for better stability when doing sports
    [left_temple.FCStd, right_temple.FCStd]
